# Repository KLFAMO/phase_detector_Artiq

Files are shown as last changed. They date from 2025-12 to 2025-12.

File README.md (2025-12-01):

# Phase Detector for Frequencies from 0 to 200 MHz

## Description

This is a phase detector designed to measure phase differences for input frequencies ranging from 0 to approximately 200 MHz. The device includes configurable frequency dividers for each input channel.

An STM32 microcontroller is used to manage the operational parameters of the detector and its components. These settings can be modified via an Ethernet interface by sending specific commands to the device.

## Features

- **Frequency Range**: 0 - 200 MHz (may change, depending on chips availability)
- **Configurable Frequency Dividers** for each input channel
- **STM32 Microcontroller** to manage operational parameters
- **Ethernet Communication** for real-time configuration and monitoring
- **Outputs**:
  - Fast analog output from the phase detector
  - Slow analog output from the phase detector
  - Analog output after passing through a PI controller
- **Standards**: The device is compliant with **Sinara** and **Artic** standards, ensuring compatibility with other systems that adhere to these protocols.

## Communication

The device allows full configuration and monitoring via Ethernet. Users can send commands to the microcontroller to change parameters such as:
- Frequency divider values
- Phase detector settings
- Calibration and diagnostics

## Applications

The phase detector is suitable for a variety of applications, including:
- Laser to optical frequency comb frequency locking
- Laser to laser frequency locking.

## Documentation

Detailed documentation, including schematics, source code, and configuration instructions, will be provided in future releases of the repository.

## commands

`R 1` - read register from `ADDR`, after reading `R` is set to 0

`W 1` - write to register of address `ADDR`, after writing `W` is set to 0

`RV` - red value

`WV` - value to write 

`ADDR` - register address to be red or written

## License

[MIT](https://opensource.org/licenses/MIT)

## Acknowledgments
This work has received funding from the European Partnership on Metrology, co-financed by the European Union’s Horizon Europe Research and Innovation Programme and by the Participating States, under grant number 22IEM01 TOCK.

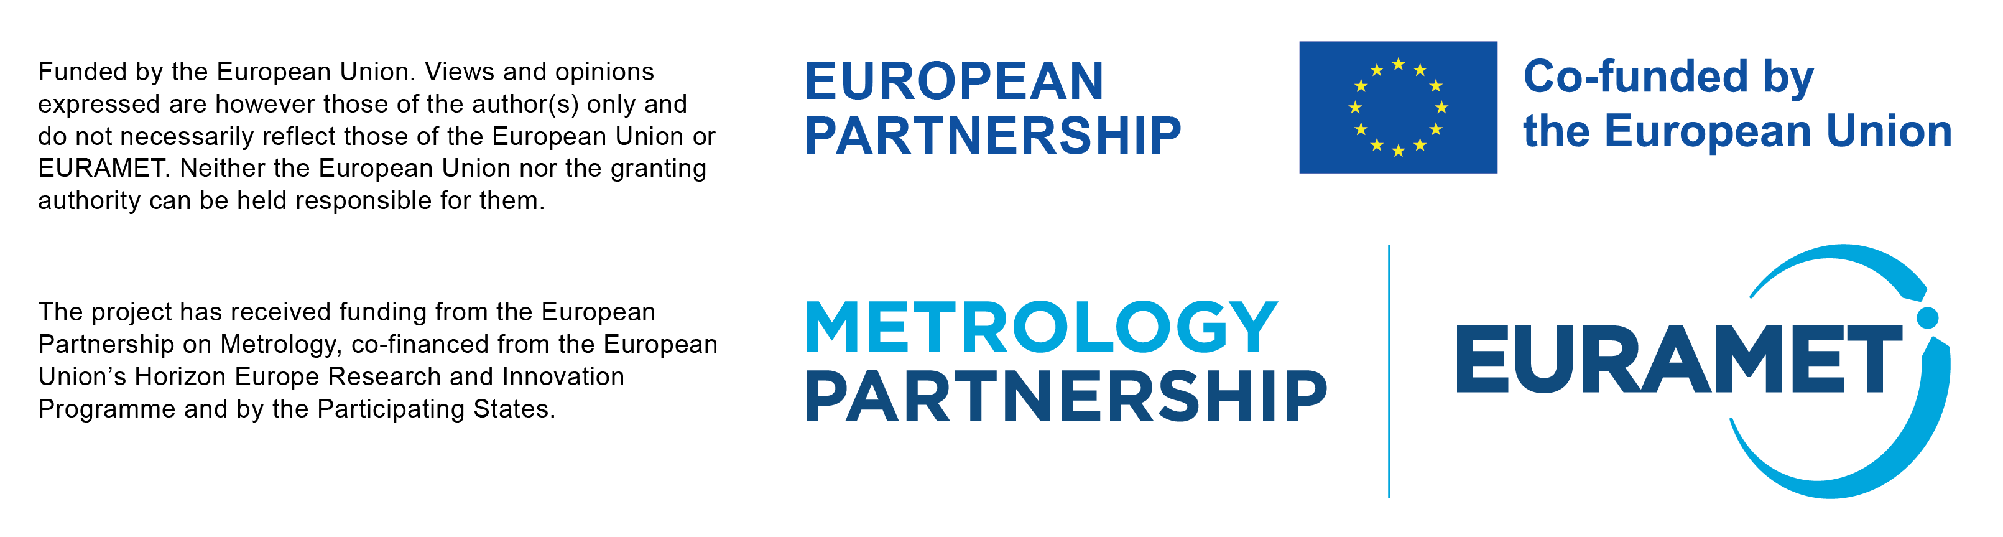
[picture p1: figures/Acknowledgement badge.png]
badge


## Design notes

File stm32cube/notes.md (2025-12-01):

2024-09-02

Checking DAC: bits to voltage

DACIN1 - [SetDAC(0, 65000);]  -> 2.955 V
DACIN1 - [SetDAC(0, 30000);]  -> 1.35 V
DACIN2 - [SetDAC(1, 25000);]  -> 1.125 V
DACIN3 - [SetDAC(2, 20000);]  -> 0.882 V
DACIN4 - [SetDAC(3, 10000);]  -> 0.425 V

Checking time factor
1st test (from Mehrdad program)
10ms in program ->  300ms

Test - transistors
val set in DAC table -> current measured by multimeter  (another board)

L1:
start: -0.1A
0.0V -> 0.1A
0.1V -> -0.11A (-0.42A)
1.0V -> -0.18A (-0.94A)
2.0V -> -0.38A
-1.0V -> 0.2A
-2.0V -> 0.4A (1.89A)

L2:
start: -0.38A
0.0V -> 0.38A
0.1V -> -0.41A (-0.4A)
1.0V -> -0.93A (-0.92A)
2.0V -> -1.85
-1.0V -> 0.93A
-2.0V -> 1.86A (1.85A)

L3:
start: -0.36A
0.0V -> -0.36A
0.1V -> -0.39A (-0.39A)
1.0V -> -0.9A (-0.89A)
2.0V -> -1.8A
-1.0V -> 0.9A 
-2.0V -> 1.8A (1.79A)

2024-09-03
cur1, cur2 and cur3 = 5mV if no current applied (just after starting uC and without load and high power supply)

L1: DAC_set=0V -> DACIN1_mes=0.48V

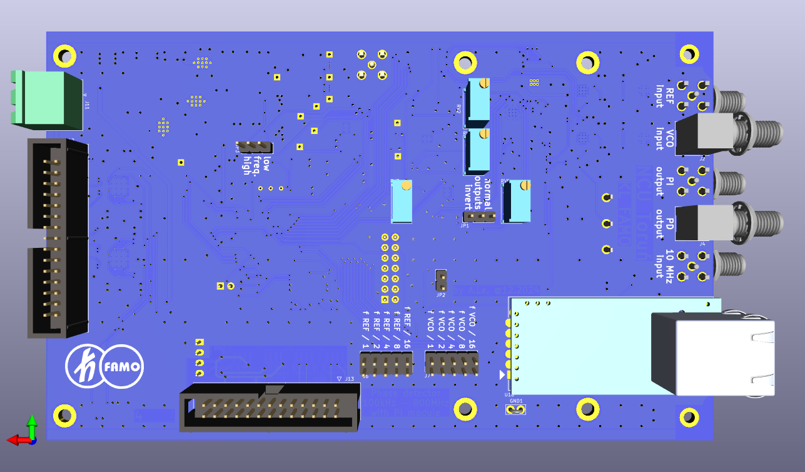
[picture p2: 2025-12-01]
kicad/model/HF_phase_detector_bottom.png

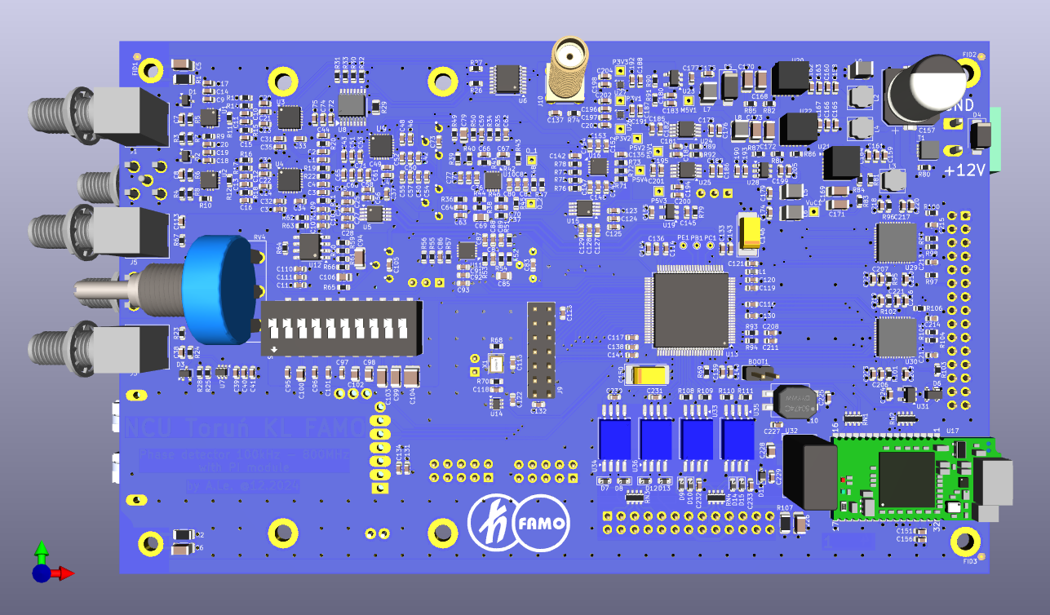
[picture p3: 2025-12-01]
kicad/model/HF_phase_detector_top.png

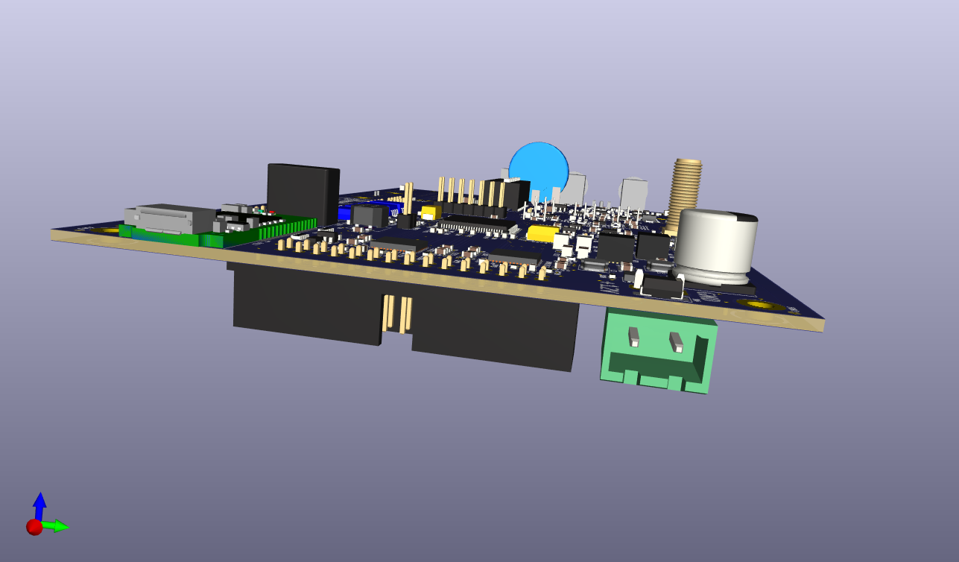
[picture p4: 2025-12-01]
kicad/model/HF_phase_detector_right.png

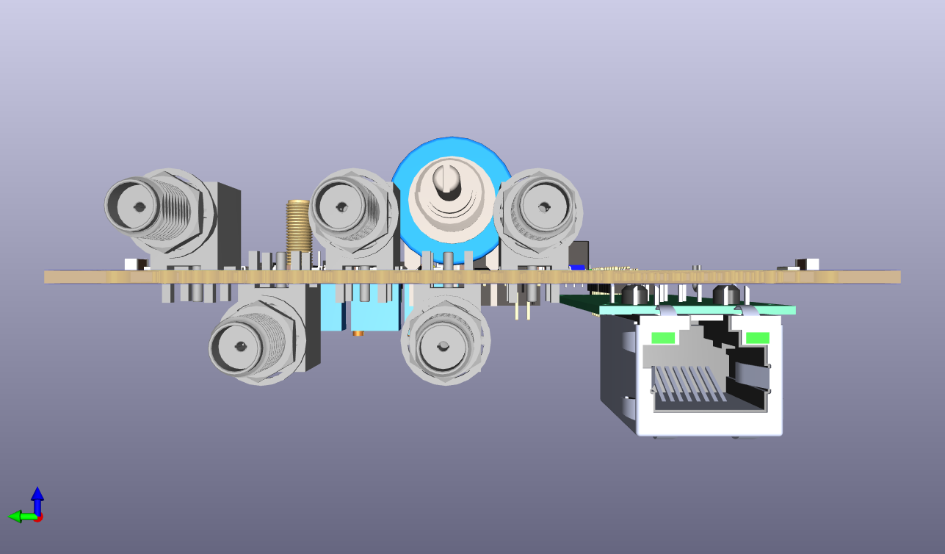
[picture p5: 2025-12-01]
kicad/model/HF_phase_detector_left.png

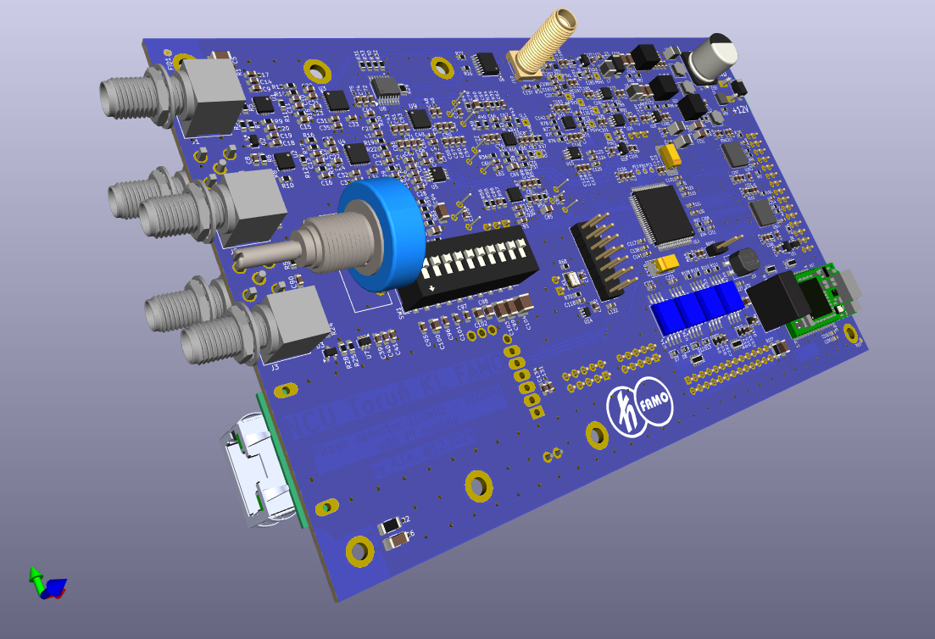
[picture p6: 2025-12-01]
kicad/model/HF_phase_detector.png

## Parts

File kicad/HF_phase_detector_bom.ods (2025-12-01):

Source: | D:\Projekty\FAMO\HF_phase_detector\HF_phase_detector.kicad_sch
Date: | 07.01.2025 11:11:47
Tool: | Eeschema 7.0.11
Generator: | C:\Program Files\KiCad\bin\scripting\plugins/bom_csv_grouped_by_value.py
Component Count: | 429
Item | Qty | Reference(s) | Value | LibPart | Footprint | Datasheet | Comm | Sim.Device | Sim.Enable | Sim.Pins
1 | 0 | BOOT1 | DNP | Connector_Generic:Conn_01x02 | Connector_PinHeader_2.54mm:PinHeader_1x02_P2.54mm_Vertical | ~ | igły 2x1x2,54
2 | 16 | C1, C2, C3, C4, C7, C8, C10, C11, C12, C13, C15, C16, C25, C26, C27, C28 | 15n 25V C0G | Device:C | Capacitor_SMD:C_0603_1608Metric | ~
3 | 3 | C5, C6, C226 | GCJ31BR73A102KXJ1L | Device:C | Capacitor_SMD:C_1206_3216Metric | ~ | 1n 1kV X7R
4 | 14 | C9, C18, C39, C72, C76, C80, C87, C91, C107, C110, C123, C127, C147, C152 | 100p 50V C0G | Device:C | Capacitor_SMD:C_0603_1608Metric | ~
5 | 78 | C14, C19, C21, C22, C23, C24, C31, C32, C33, C34, C37, C40, C46, C47, C50, C51, C57, C58, C64, C68, C74, C77, C81, C88, C92, C108, C111, C115, C116, C119, C122, C124, C128, C130, C133, C134, C136, C138, C139, C148, C151, C153, C155, C163, C164, C167, C177, C178, C180, C181, C182, C189, C191, C192, C193, C194, C195, C196, C197, C198, C199, C206, C207, C209, C210, C212, C213, C214, C215, C216, C217, C218, C219, C224, C230, C231, C232, C233 | 100n 50V X7R | Device:C | Capacitor_SMD:C_0603_1608Metric | ~
6 | 58 | C17, C20, C29, C30, C35, C36, C41, C42, C43, C55, C56, C63, C65, C73, C75, C78, C82, C83, C89, C93, C105, C109, C112, C121, C125, C126, C129, C131, C132, C140, C144, C149, C154, C156, C174, C175, C176, C179, C183, C184, C185, C186, C187, C188, C190, C200, C201, C202, C203, C204, C205, C220, C221, C222, C223, C225, C227, C229 | GRM188R61E106KA73 | Device:C | Capacitor_SMD:C_0603_1608Metric | ~ | 10uF 25V X5R
7 | 10 | C38, C48, C49, C52, C53, C54, C60, C61, C71, C90 | 1n 50V C0G | Device:C | Capacitor_SMD:C_0603_1608Metric | ~
8 | 0 | C44, C45 | DNP | Device:C | Capacitor_SMD:C_0603_1608Metric | ~ | 15n 25V C0G
9 | 4 | C59, C62, C113, C137 | 220p 50V C0G | Device:C | Capacitor_SMD:C_0603_1608Metric | ~
10 | 3 | C66, C67, C70 | ECH-U1C221JX5 | Device:C | Capacitor_SMD:C_0603_1608Metric | ~ | 220p 11V film
11 | 4 | C69, C79, C85, C106 | GRMJN65C1H104... | Device:C | Capacitor_SMD:C_0805_2012Metric | ~ | 100n 50V C0G 0704
12 | 4 | C84, C86, C135, C142 | 22p 50V C0G | Device:C | Capacitor_SMD:C_0603_1608Metric | ~
13 | 2 | C94, C103 | ECH-U1C223JX5 | Device:C | Capacitor_SMD:C_1206_3216Metric | ~ | 22n 16V film
14 | 1 | C95 | ECH-U1C101GX5 | Device:C | Capacitor_SMD:C_0603_1608Metric | ~ | 100p 16V film
15 | 1 | C96 | ECH-U1C471GX5 | Device:C | Capacitor_SMD:C_0603_1608Metric | ~ | 470p 16V film
16 | 1 | C97 | ECH-U1C222GX5 | Device:C | Capacitor_SMD:C_0603_1608Metric | ~ | 2,2n 16V film
17 | 1 | C98 | ECH-U1C103JX5 | Device:C | Capacitor_SMD:C_0805_2012Metric | ~ | 10n 16V film
18 | 1 | C99 | ECH-U1C473GX5 | Device:C | Capacitor_SMD:C_1206_3216Metric | ~ | 47n 16V film
19 | 1 | C100 | ECH-U1H221GX5 | Device:C | Capacitor_SMD:C_0805_2012Metric | ~ | 220p 50V film
20 | 1 | C101 | ECH-U1C102JX5 | Device:C | Capacitor_SMD:C_0603_1608Metric | ~ | 1n 16V film
21 | 1 | C102 | ECH-U1C472GX5 | Device:C | Capacitor_SMD:C_0805_2012Metric | ~ | 4,7n 16V film
22 | 1 | C104 | ECH-U1C104GX5 | Device:C | Capacitor_SMD:C_1210_3225Metric | ~ | 100n 16V film
23 | 2 | C114, C117 | 2u2 10V X7R | Device:C | Capacitor_SMD:C_0603_1608Metric | ~
24 | 2 | C118, C145 | 15p 50V C0G | Device:C | Capacitor_SMD:C_0603_1608Metric | ~
25 | 3 | C120, C141, C143 | GCM188R71E105KA64J | Device:C | Capacitor_SMD:C_0603_1608Metric | ~ | 1uF 25V X7R
26 | 2 | C146, C150 | 293D107X9010C2TE3 | Device:C_Polarized | Capacitor_Tantalum_SMD:CP_EIA-7132-28_AVX-C | ~ | 100u 6,3V tantal case C
27 | 1 | C157 | AEA1010471M025R | Device:C_Polarized | Capacitor_SMD:CP_Elec_10x10 | ~ | ≥ 470u, ≥ 20V, ≥ 5000h
28 | 7 | C158, C159, C160, C161, C162, C165, C166 | GRM188R6YA106MA73 | Device:C | Capacitor_SMD:C_0603_1608Metric | ~ | 10uF 35V X5R
29 | 6 | C168, C169, C170, C171, C172, C173 | GRM31CR61A476KE15L | Device:C | Capacitor_SMD:C_1206_3216Metric | ~ | 47u 10V X5R
30 | 2 | C208, C211 | 82p 50V C0G | Device:C | Capacitor_SMD:C_0603_1608Metric | ~
31 | 1 | C228 | 1n 100V C0G | Device:C | Capacitor_SMD:C_0805_2012Metric | ~
32 | 3 | D1, D2, D3 | BAT54SW... | Diode:BAT54S | Package_TO_SOT_SMD:SOT-323_SC-70 | https://assets.nexperia.com/documents/data-sheet/BAT54SW.pdf
33 | 1 | D4 | SMAJ15AC | Diode:SD12_SOD323 | Diode_SMD:D_SMA | https://www.littelfuse.com/~/media/electronics/datasheets/tvs_diode_arrays/littelfuse_tvs_diode_array_sd_c_datasheet.pdf.pdf
34 | 1 | D5 | STPS2L30A | Device:D_Schottky_Filled | Diode_SMD:D_SMA | ~
35 | 1 | D6 | WE 8240136 | Power_Protection:PRTR5V0U2X | Package_TO_SOT_SMD:SOT-143 | https://assets.nexperia.com/documents/data-sheet/PRTR5V0U2X.pdf | PRTR5V0U2X
36 | 8 | D7, D8, D9, D10, D12, D13, D14, D15 | TS4148C RZG | Device:D_Filled | Diode_SMD:D_0603_1608Metric | ~ |  | D |  | 1=K 2=A
37 | 1 | D11 | SD05.TCT | c3Av2_A-rescue:D_Zener_ALT-Device | Diode_SMD:D_SOD-323
42 | 5 | J1, J2, J3, J4, J5 | RF2-49B-T-00-50-G-HDW | Connector:Conn_Coaxial | Connector_Coaxial:SMA_Amphenol_132203-12_Horizontal | ~ | '132203
43 | 2 | J6, J7 | igły 2x5x2,54mm | Connector_Generic:Conn_02x05_Odd_Even | Connector_PinHeader_2.54mm:PinHeader_2x05_P2.54mm_Vertical | ~
44 | 0 | J9 | DNP | Connector_Generic:Conn_02x07_Odd_Even | Connector_PinHeader_2.54mm:PinHeader_2x07_P2.54mm_Vertical | ~ | igły 2x7x2,54mm
45 | 1 | J10 | SMA6251A1-3GT50G-50 | Connector:Conn_Coaxial | Connector_Coaxial:SMA_Amphenol_132291-12_Vertical | ~
46 | 1 | J11 | MSTBA 2,5/ 2-G-5,08 1757242 | Connector_Generic:Conn_01x02 | Connector_Phoenix_MSTB:PhoenixContact_MSTBA_2,5_2-G-5,08_1x02_P5.08mm_Horizontal | ~
47 | 1 | J12 | N2530-6002-RB | Connector_Generic:Conn_02x15_Odd_Even | Connector_IDC:IDC-Header_2x15_P2.54mm_Vertical | ~
48 | 1 | J13 | N2526-6002RB | Connector:Conn_01x26_Pin | Connector_IDC:IDC-Header_2x13_P2.54mm_Vertical | ~
49 | 2 | JP1, JP3 | igły 1x3x2,54mm | Jumper:Jumper_3_Open | Connector_PinHeader_2.54mm:PinHeader_1x03_P2.54mm_Vertical | ~
50 | 1 | JP2 | igły 1x2x2,54mm | ff:Jumper_2_Open | Connector_PinHeader_2.54mm:PinHeader_1x02_P2.54mm_Vertical | ~
51 | 1 | L1 | LQM18DN330M70L | Device:L | Inductor_SMD:L_0603_1608Metric | ~ | LQM18DZ330M70L
52 | 3 | L2, L3, L4 | LQH44NN101K03L | Device:L_Ferrite | ff_lib_7:L_MURATA_LQH44 | ~ | ≥ 100uH, >200mA
53 | 5 | L5, L6, L7, L8, L9 | LQH32PN100MNCL | Device:L_Ferrite | Inductor_SMD:L_1210_3225Metric | ~ | ≥ 10uH, ≥ 500mA, 1210
54 | 1 | L10 | 50225C Murata | c100AvA-rescue:L_Core_Ferrite_Coupled_1423-Device | ff_lib_7:L_CommonMode_Murata_5000 | https://www.murata-ps.com/pub/data/magnetics/kmp_5000c.pdf | or 50475C
57 | 2 | R1, R2 | CHV1206-FX-1004E | Device:R | Resistor_SMD:R_1206_3216Metric | ~ | HV732BTTD1004F
58 | 6 | R3, R4, R23, R58, R67, R74 | 49,9R 1% | Device:R | Resistor_SMD:R_0603_1608Metric | ~
59 | 6 | R5, R6, R7, R8, R24, R25 | 680R 1% | Device:R | Resistor_SMD:R_0603_1608Metric | ~
60 | 3 | R9, R10, R28 | 150k 1% | Device:R | Resistor_SMD:R_0603_1608Metric | ~
61 | 16 | R11, R12, R70, R79, R95, R96, R97, R98, R99, R100, R101, R102, R103, R104, R105, R106 | 100R 1% | Device:R | Resistor_SMD:R_0603_1608Metric | ~
62 | 2 | R13, R16 | 49,9k 1% | Device:R | Resistor_SMD:R_0603_1608Metric | ~
63 | 9 | R14, R15, R17, R18, R69, R108, R109, R110, R111 | 1k 1% | Device:R | Resistor_SMD:R_0603_1608Metric | ~
64 | 12 | R19, R20, R21, R22, R32, R33, R34, R35, R37, R40, R43, R45 | 200R 1% | Device:R | Resistor_SMD:R_0603_1608Metric | ~
65 | 2 | R26, R27 | 60,4k 1% | Device:R | Resistor_SMD:R_0603_1608Metric | ~
66 | 1 | R29 | 200R 1% | Device:R | Resistor_SMD:R_0805_2012Metric | ~
67 | 2 | R30, R31 | 10R 1% | Device:R | Resistor_SMD:R_0603_1608Metric | ~
68 | 7 | R36, R38, R47, R48, R53, R55, R57 | 3k6 1% | Device:R | Resistor_SMD:R_0603_1608Metric | ~
69 | 5 | R39, R41, R42, R44, R46 | 36k 1% | Device:R | Resistor_SMD:R_0603_1608Metric | ~
70 | 18 | R49, R50, R52, R54, R65, R66, R68, R71, R72, R73, R75, R78, R80, R82, R83, R87, R89, R92 | 10k 1% | Device:R | Resistor_SMD:R_0603_1608Metric | ~
71 | 2 | R51, R56 | 1k2 1% | Device:R | Resistor_SMD:R_0603_1608Metric | ~
72 | 1 | R59 | 475R 1% | Device:R | Resistor_SMD:R_0603_1608Metric | ~
73 | 1 | R60 | 965R 1% | Device:R | Resistor_SMD:R_0603_1608Metric | ~
74 | 1 | R61 | 4,75k 1% | Device:R | Resistor_SMD:R_0603_1608Metric | ~
75 | 5 | R62, R63, R64, R81, R86 | 100k 1% | Device:R | Resistor_SMD:R_0603_1608Metric | ~
76 | 2 | R76, R77 | 30k 1% | Device:R | Resistor_SMD:R_0603_1608Metric | ~
77 | 2 | R84, R85 | 4,32k 1% | Device:R | Resistor_SMD:R_0603_1608Metric | ~
78 | 1 | R88 | 2,26k 1% | Device:R | Resistor_SMD:R_0603_1608Metric | ~
79 | 1 | R90 | 22k 1% | Device:R | Resistor_SMD:R_0603_1608Metric | ~
80 | 1 | R91 | 70,6k 1% | Device:R | Resistor_SMD:R_0603_1608Metric | ~
81 | 2 | R93, R94 | 220R 1% | Device:R | Resistor_SMD:R_0603_1608Metric | ~
82 | 1 | R107 | HV732BTTD1004F | Device:R | Resistor_SMD:R_1206_3216Metric | ~
83 | 2 | RN1, RN2 | CAT16-220J4LF | Device:R_Pack04 | Resistor_SMD:R_Array_Concave_4x0603 | ~
84 | 1 | RN3 | CAT16-102J4LF | Device:R_Pack04 | Resistor_SMD:R_Array_Concave_4x0603 | ~
85 | 1 | RN4 | CAT16-471J4LF | Device:R_Pack04 | Resistor_SMD:R_Array_Concave_4x0603 | ~
86 | 1 | RV1 | 3296Y-1-502LF | Device:R_Potentiometer | Potentiometer_THT:Potentiometer_Bourns_3296Y_Vertical | ~ | T93YB103KT20
87 | 3 | RV2, RV3, RV5 | 3296Y-1-103LF | Device:R_Potentiometer | Potentiometer_THT:Potentiometer_Bourns_3296Y_Vertical | ~ | T93YB103KT20
88 | 1 | RV4 | 3856A-286-103AL | PID_FAMO_v2-rescue:R_POT-Device | ff_lib_7:Potentiometer_Bourns_3856A-286_horizontal | https://www.bourns.com/docs/Product-Datasheets/385126.pdf
89 | 1 | SW1 | A6S-0101-H | Switch:SW_DIP_x10 | Button_Switch_SMD:SW_DIP_SPSTx10_Slide_9.78x27.58mm_W8.61mm_P2.54mm | ~
90 | 1 | T1 | DMP3007SFG-7 | Transistor_FET:DMP3013SFV | ff_lib_7:Diodes_PowerDI3333-8 | https://www.diodes.com/assets/Datasheets/DMP3007SFG.pdf | DMP4013LFG-7
91 | 2 | U1, U2 | TLV3605RVKx | Comparator:LTC6754xUD | Package_DFN_QFN:QFN-12-1EP_3x3mm_P0.5mm_EP1.65x1.65mm_ThermalVias | https://www.ti.com/lit/ds/symlink/tlv3604.pdf
92 | 2 | U3, U4 | CDCM1804RGET | ff:CDCM1804RGET | Package_DFN_QFN:QFN-24-1EP_4x4mm_P0.5mm_EP2.15x2.15mm_ThermalVias | https://www.ti.com/lit/ds/symlink/cdcm1804.pdf
93 | 1 | U5 | LVELT23 | ff:LVELT23 | Package_SO:MSOP-8_3x3mm_P0.65mm | https://www.ti.com/lit/ds/symlink/sn65lvelt23.pdf
94 | 1 | U6 | TBD62003AFNG,EL | Transistor_Array:ULN2003 | Package_SO:SSOP-16_4.4x5.2mm_P0.65mm | https://toshiba.semicon-storage.com/info/TBD62003AFG_datasheet_en_20150724.pdf
95 | 1 | U7 | TLV3603DCKx | Comparator:LTC6752xSC6-1 | Package_TO_SOT_SMD:SOT-363_SC-70-6 | https://www.ti.com/lit/ds/symlink/tlv3601.pdf
96 | 1 | U8 | HMC439QS16GE(TR) | ff:HMC439QS16G | ff_lib_7:QS16GE_ADI | https://www.analog.com/media/en/technical-documentation/data-sheets/hmc439.pdf
97 | 1 | U9 | HMC984LP4E | ff:HMC984LP4E | Package_DFN_QFN:QFN-24-1EP_4x4mm_P0.5mm_EP2.8x2.8mm_ThermalVias | https://www.analog.com/media/en/technical-documentation/data-sheets/hmc984.pdf | https://www.analog.com/media/en/technical-documentation/evaluation-documentation/hmc983lp5e_eval_pcb_schematic.pdf
98 | 3 | U10, U11, U16 | OPA2863AIDSNR | Amplifier_Operational:LTC6269xDD | Package_DFN_QFN:DFN-10-1EP_3x3mm_P0.5mm_EP1.65x2.38mm_ThermalVias | https://www.ti.com/lit/ds/symlink/opa2863a.pdf
99 | 1 | U12 | OPA2206ADR | Amplifier_Operational:OPA2277 | Package_SO:SOIC-8_3.9x4.9mm_P1.27mm | https://www.ti.com/lit/ds/symlink/opa2206.pdf
100 | 1 | U13 | STM32H743VITx | MCU_ST_STM32H7:STM32H743VITx | Package_QFP:LQFP-100_14x14mm_P0.5mm | https://www.st.com/resource/en/datasheet/stm32h743vi.pdf
101 | 1 | U14 | 74AUP1G157GW,125 | ff:1G157 | Package_TO_SOT_SMD:SOT-363_SC-70-6 | https://assets.nexperia.com/documents/data-sheet/74AUP1G157.pdf
102 | 1 | U15 | DAC8550IxDGK | Analog_DAC:DAC8550IxDGK | Package_SO:MSOP-8_3x3mm_P0.65mm | https://www.ti.com/lit/ds/symlink/dac8550.pdf
103 | 1 | U17 | STLINK-V3MODS | ff:STLINK-V3MODS | ff_lib_7:STLINK-V3MODS | https://www.st.com/content/ccc/resource/technical/document/user_manual/group1/00/14/17/68/0f/01/48/01/DM00555046/files/DM00555046.pdf/jcr:content/translations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
104 | 1 | U18 | USR-TCP232-T2 | ff:USR-TCP232-T2 | ff_lib_7:USR-TC232-T2
105 | 2 | U19, U31 | 24AA02E48T-I/OT | Memory_EEPROM:24AA02-OT | Package_TO_SOT_SMD:SOT-23-5 | https://ww1.microchip.com/downloads/en/DeviceDoc/24AA02E48-24AA025E48-24AA02E64-24AA025E64-Data-Sheet-20002124H.pdf
106 | 3 | U20, U21, U22 | TPSM5601R5Hx | ff:TPSM5601R5HRDAR | ff_lib_7:15-B3QFN (5x5,5) | https://www.ti.com/lit/ds/symlink/tpsm5601r5he.pdf
107 | 1 | U23 | TPS72301DBV | ff:TPS72301DBV | Package_TO_SOT_SMD:SOT-23-5 | http://www.ti.com/lit/ds/symlink/tps723.pdf
108 | 2 | U24, U25 | LP2966IMM-5050/NOPB | ff:LP2966IMM-5050_NOPB | Package_SO:VSSOP-8_3.0x3.0mm_P0.65mm | https://www.ti.com/lit/ds/symlink/lp2966.pdf
109 | 2 | U26, U27 | TLV7163030PDPQT | ff:TLV7163030PDPQT | ff_lib_7:DFN-6-1EP_1.2x1.2mm_P0.4mm_EP0.3x0.94mm_ff | https://www.ti.com/lit/ds/symlink/tlv716p.pdf
110 | 1 | U28 | REF3450TIDBVR | ff:REF34xxRDBVR | Package_TO_SOT_SMD:SOT-23-6 | https://www.ti.com/lit/ds/symlink/ref3425.pdf
111 | 2 | U29, U30 | SN65MLVD040RGZT | ff:SN65MLVD040 | ff_lib_7:VQFN-48-1EP_7x7mm_P0.5mm_EP4.1x4.1mm_ThermalVias | https://www.ti.com/lit/ds/symlink/sn65mlvd040.pdf
112 | 1 | U32 | CRE1S1205SC | Regulator_Switching:CRE1S1205SC | Converter_DCDC:Converter_DCDC_Murata_CRE1xxxxxxSC_THT | http://power.murata.com/datasheet?/data/power/ncl/kdc_cre1.pdf | TBA1-1211, IE1205SH
113 | 4 | U33, U34, U35, U36 | TLP2270(TP4,E | Isolator:HCPL-063A | Package_SO:SOIC-8_7.5x5.85mm_P1.27mm | https://toshiba.semicon-storage.com/info/TLP2270_datasheet_en_20191126.pdf
114 | 1 | X1 | ASE-10.000MHZ-L-C-T | Oscillator:ASE-xxxMHz | ff_lib_7:Oscillator_SMD_Abracon_ASE-4Pin_3.2x2.5mm | http://www.abracon.com/Oscillators/ASV.pdf

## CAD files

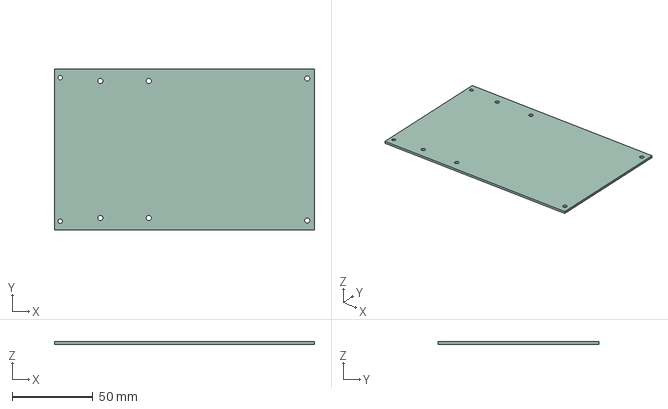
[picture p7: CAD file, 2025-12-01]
kicad/model/artiq_base.step
161.0 x 100.0 x 1.58 mm

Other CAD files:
kicad/model/artiq_base.FCStd

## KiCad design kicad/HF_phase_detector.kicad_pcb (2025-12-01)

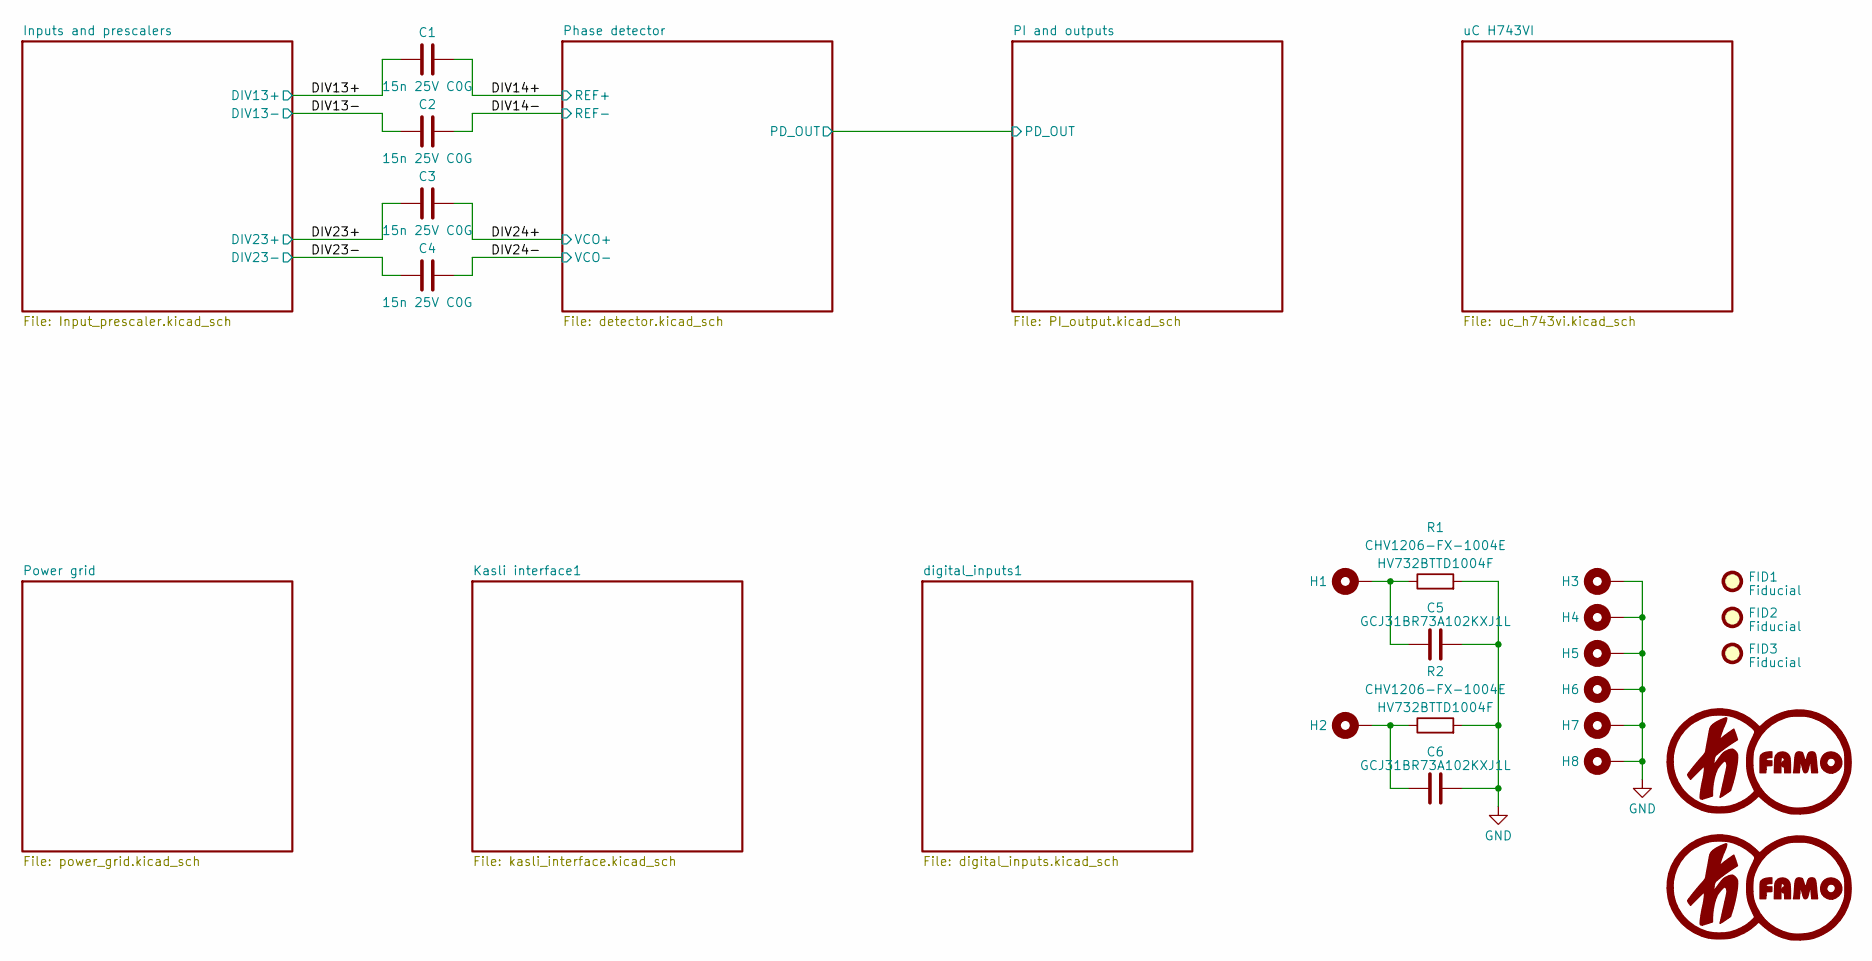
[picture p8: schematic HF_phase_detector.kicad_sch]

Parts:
C1, C2, C3, C4: 15n 25V C0G; C_0603_1608Metric
C5, C6: GCJ31BR73A102KXJ1L; C_1206_3216Metric
FID1, FID2, FID3: Fiducial; Fiducial_0.5mm_Mask1.5mm
G1, G2: LOGO; kl_famo_logo_small
H1, H2: MountingHole_Pad; MountingHole_2.7mm_M2.5_DIN965_Pad
H3, H4, H5, H6, H7, H8: MountingHole_Pad; MountingHole_3.2mm_M3_DIN965_Pad
R1, R2: CHV1206-FX-1004E; R_1206_3216Metric

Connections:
/DIV13-: C2.2; also elsewhere on the board
/DIV14-: C2.1; also elsewhere on the board
/DIV23+: C3.2; also elsewhere on the board
/DIV23-: C4.2; also elsewhere on the board
/DIV24+: C3.1; also elsewhere on the board
/DIV24-: C4.1; also elsewhere on the board
unnamed: C5.1, H1.1, R1.1
unnamed: C6.1, H2.1, R2.1

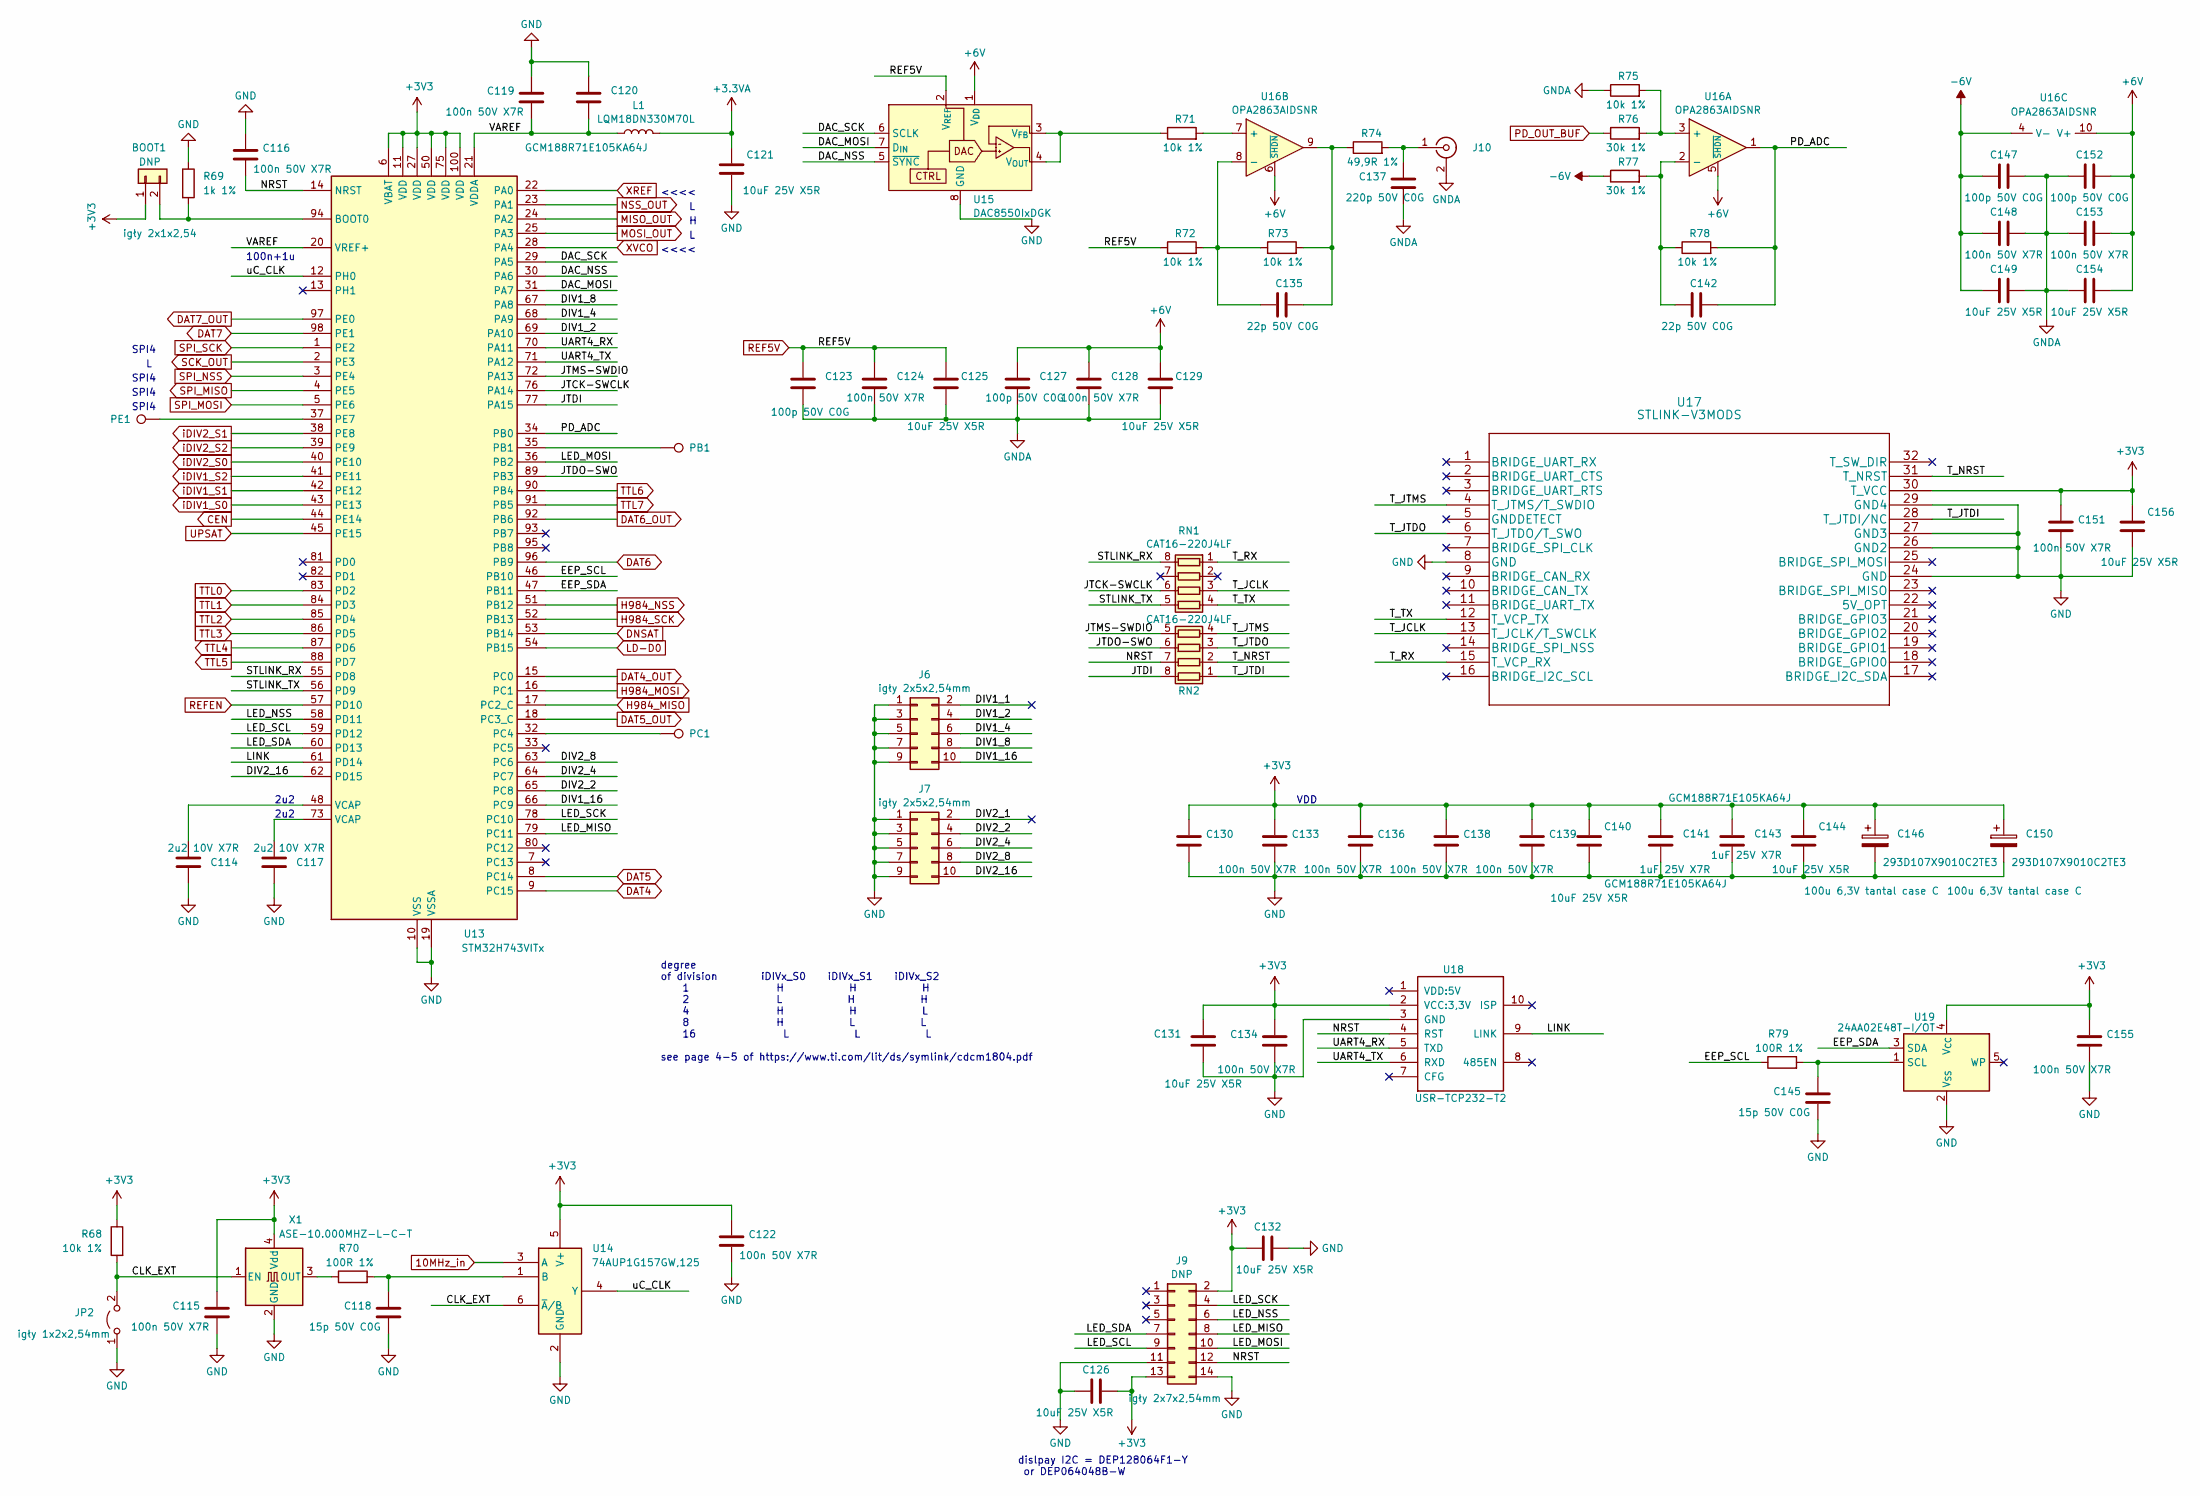
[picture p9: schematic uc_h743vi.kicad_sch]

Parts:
BOOT1: DNP; PinHeader_1x02_P2.54mm_Vertical
C114, C117: 2u2 10V X7R; C_0603_1608Metric
C115, C116, C119, C122, C124, C128, C130, C133, C134, C136, C138, C139, C148, C151, C153, C155: 100n 50V X7R; C_0603_1608Metric
C118, C145: 15p 50V C0G; C_0603_1608Metric
C120, C141, C143: GCM188R71E105KA64J; C_0603_1608Metric
C121, C125, C126, C129, C131, C132, C140, C144, C149, C154, C156: GRM188R61E106KA73; C_0603_1608Metric
C123, C127, C147, C152: 100p 50V C0G; C_0603_1608Metric
C135, C142: 22p 50V C0G; C_0603_1608Metric
C137: 220p 50V C0G; C_0603_1608Metric
C146, C150: 293D107X9010C2TE3; CP_EIA-7132-28_AVX-C
J6, J7: igły 2x5x2,54mm; PinHeader_2x05_P2.54mm_Vertical
J9: DNP; PinHeader_2x07_P2.54mm_Vertical
J10: SMA6251A1-3GT50G-50; SMA_Amphenol_132291-12_Vertical
JP2: igły 1x2x2,54mm; PinHeader_1x02_P2.54mm_Vertical
L1: LQM18DN330M70L; L_0603_1608Metric
PB1: TestPoint; TestPoint_THTPad_D1.0mm_Drill0.5mm
PC1: TestPoint; TestPoint_THTPad_D1.0mm_Drill0.5mm
PE1: TestPoint; TestPoint_THTPad_D1.0mm_Drill0.5mm
R68, R71, R72, R73, R75, R78: 10k 1%; R_0603_1608Metric
R69: 1k 1%; R_0603_1608Metric
R70, R79: 100R 1%; R_0603_1608Metric
R74: 49,9R 1%; R_0603_1608Metric
R76, R77: 30k 1%; R_0603_1608Metric
RN1, RN2: CAT16-220J4LF; R_Array_Concave_4x0603
U13: STM32H743VITx; LQFP-100_14x14mm_P0.5mm
U14: 74AUP1G157GW,125; SOT-363_SC-70-6
U15: DAC8550IxDGK; MSOP-8_3x3mm_P0.65mm
U16: OPA2863AIDSNR; DFN-10-1EP_3x3mm_P0.5mm_EP1.65x2.38mm_ThermalVias
U17: STLINK-V3MODS
U18: USR-TCP232-T2; USR-TC232-T2
U19: 24AA02E48T-I/OT; SOT-23-5
X1: ASE-10.000MHZ-L-C-T; Oscillator_SMD_Abracon_ASE-4Pin_3.2x2.5mm

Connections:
10MHz_in: U14.3 (A); also elsewhere on the board
/uC H743VI/CLK_EXT: JP2.2 (B), R68.2, U14.6 (~A/B), X1.1 (EN)
/uC H743VI/DAC_MOSI: U13.31 (PA7), U15.7 (D_{IN})
/uC H743VI/DAC_NSS: U13.30 (PA6), U15.5 (~SYNC)
/uC H743VI/DAC_SCK: U13.29 (PA5), U15.6 (SCLK)
/uC H743VI/DIV1_1: J6.2
/uC H743VI/DIV1_2: J6.4, U13.69 (PA10)
/uC H743VI/DIV1_4: J6.6, U13.68 (PA9)
/uC H743VI/DIV1_8: J6.8, U13.67 (PA8)
/uC H743VI/DIV1_16: J6.10, U13.66 (PC9)
/uC H743VI/DIV2_1: J7.2
/uC H743VI/DIV2_2: J7.4, U13.65 (PC8)
/uC H743VI/DIV2_4: J7.6, U13.64 (PC7)
/uC H743VI/DIV2_8: J7.8, U13.63 (PC6)
/uC H743VI/DIV2_16: J7.10, U13.62 (PD15)
/uC H743VI/EEP_SCL: R79.1, U13.46 (PB10)
/uC H743VI/EEP_SDA: U13.47 (PB11), U19.3 (SDA)
/uC H743VI/JTCK-SWCLK: RN1.6 (R3.2), U13.76 (PA14)
/uC H743VI/JTDI: RN2.8 (R1.2), U13.77 (PA15)
/uC H743VI/JTDO-SWO: RN2.6 (R3.2), U13.89 (PB3)
/uC H743VI/JTMS-SWDIO: RN2.5 (R4.2), U13.72 (PA13)
/uC H743VI/LED_MISO: J9.8, U13.79 (PC11)
/uC H743VI/LED_MOSI: J9.10, U13.36 (PB2)
/uC H743VI/LED_NSS: J9.6, U13.58 (PD11)
/uC H743VI/LED_SCK: J9.4, U13.78 (PC10)
/uC H743VI/LED_SCL: J9.9, U13.59 (PD12)
/uC H743VI/LED_SDA: J9.7, U13.60 (PD13)
/uC H743VI/LINK: U13.61 (PD14), U18.9 (LINK)
/uC H743VI/NRST: C116.2, J9.12, RN2.7 (R2.2), U13.14 (NRST), U18.4 (RST)
/uC H743VI/STLINK_RX: RN1.8 (R1.2), U13.55 (PD8)
/uC H743VI/STLINK_TX: RN1.5 (R4.2), U13.56 (PD9)
/uC H743VI/T_JCLK: RN1.3 (R3.1), U17.13 (T_JCLK/T_SWCLK)
/uC H743VI/T_JTDI: RN2.1 (R1.1), U17.28 (T_JTDI/NC)
/uC H743VI/T_JTDO: RN2.3 (R3.1), U17.6 (T_JTDO/T_SWO)
/uC H743VI/T_JTMS: RN2.4 (R4.1), U17.4 (T_JTMS/T_SWDIO)
/uC H743VI/T_NRST: RN2.2 (R2.1), U17.31 (T_NRST)
/uC H743VI/T_RX: RN1.1 (R1.1), U17.15 (T_VCP_RX)
/uC H743VI/T_TX: RN1.4 (R4.1), U17.12 (T_VCP_TX)
/uC H743VI/UART4_RX: U13.70 (PA11), U18.5 (TXD)
/uC H743VI/UART4_TX: U13.71 (PA12), U18.6 (RXD)
/uC H743VI/uC_CLK: U13.12 (PH0), U14.4 (Y)
CEN: U13.44 (PE14); also elsewhere on the board
DAT4: U13.9 (PC15); also elsewhere on the board
DAT4_OUT: U13.15 (PC0); also elsewhere on the board
DAT5: U13.8 (PC14); also elsewhere on the board
DAT5_OUT: U13.18 (PC3_C); also elsewhere on the board
DAT6: U13.96 (PB9); also elsewhere on the board
DAT6_OUT: U13.92 (PB6); also elsewhere on the board
DAT7: U13.98 (PE1); also elsewhere on the board
DAT7_OUT: U13.97 (PE0); also elsewhere on the board
DNSAT: U13.53 (PB14); also elsewhere on the board
H984_MISO: U13.17 (PC2_C); also elsewhere on the board
H984_MOSI: U13.16 (PC1); also elsewhere on the board
H984_NSS: U13.51 (PB12); also elsewhere on the board
H984_SCK: U13.52 (PB13); also elsewhere on the board
LD-D0: U13.54 (PB15); also elsewhere on the board
MISO_OUT: U13.24 (PA2); also elsewhere on the board
MOSI_OUT: U13.25 (PA3); also elsewhere on the board
NSS_OUT: U13.23 (PA1); also elsewhere on the board
unnamed: BOOT1.2, R69.2, U13.94 (BOOT0)
unnamed: C114.2, U13.48 (VCAP)
unnamed: C117.2, U13.73 (VCAP)
unnamed: C135.2, R73.2, R74.1, U16.9
unnamed: C137.2, J10.1 (In), R74.2
unnamed: PB1.1, U13.35 (PB1)
unnamed: PC1.1, U13.32 (PC4)
unnamed: PE1.1, U13.37 (PE7)
unnamed: C118.1, R70.2, U14.1 (B)
unnamed: R71.1, U15.3 (V_{FB}), U15.4 (V_{OUT})
unnamed: R75.2, R76.2, U16.3 (+)
unnamed: R71.2, U16.7 (+)
unnamed: C135.1, R72.2, R73.1, U16.8 (-)
unnamed: C145.1, R79.2, U19.1 (SCL)
unnamed: R70.1, X1.3 (OUT)
PD_OUT_BUF: R76.1; also elsewhere on the board
REF5V: C123.2, C124.2, C125.2, R72.1, U15.2 (V_{REF}); also elsewhere on the board
REFEN: U13.57 (PD10); also elsewhere on the board
SCK_OUT: U13.2 (PE3); also elsewhere on the board
SPI_MISO: U13.4 (PE5); also elsewhere on the board
SPI_MOSI: U13.5 (PE6); also elsewhere on the board
SPI_NSS: U13.3 (PE4); also elsewhere on the board
SPI_SCK: U13.1 (PE2); also elsewhere on the board
TTL0: U13.83 (PD2); also elsewhere on the board
TTL1: U13.84 (PD3); also elsewhere on the board
TTL2: U13.85 (PD4); also elsewhere on the board
TTL3: U13.86 (PD5); also elsewhere on the board
TTL4: U13.87 (PD6); also elsewhere on the board
TTL5: U13.88 (PD7); also elsewhere on the board
TTL6: U13.90 (PB4); also elsewhere on the board
TTL7: U13.91 (PB5); also elsewhere on the board
UPSAT: U13.45 (PE15); also elsewhere on the board
XREF: U13.22 (PA0); also elsewhere on the board
XVCO: U13.28 (PA4); also elsewhere on the board
iDIV1_S0: U13.43 (PE13); also elsewhere on the board
iDIV1_S1: U13.42 (PE12); also elsewhere on the board
iDIV1_S2: U13.41 (PE11); also elsewhere on the board
iDIV2_S0: U13.40 (PE10); also elsewhere on the board
iDIV2_S1: U13.38 (PE8); also elsewhere on the board
iDIV2_S2: U13.39 (PE9); also elsewhere on the board

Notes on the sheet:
VDD
2u2
<<<<
dislpay I2C = DEP128064F1-Y or DEP064048B-W
SPI4
100n+1u
degree of division iDIVx_S0 iDIVx_S1 iDIVx_S2 1 H H H 2 L H H 4 H H L 8 H L L 16 L L L see page 4-5 of https://www.ti.com/lit/ds/symlink/cdcm1804.pdf

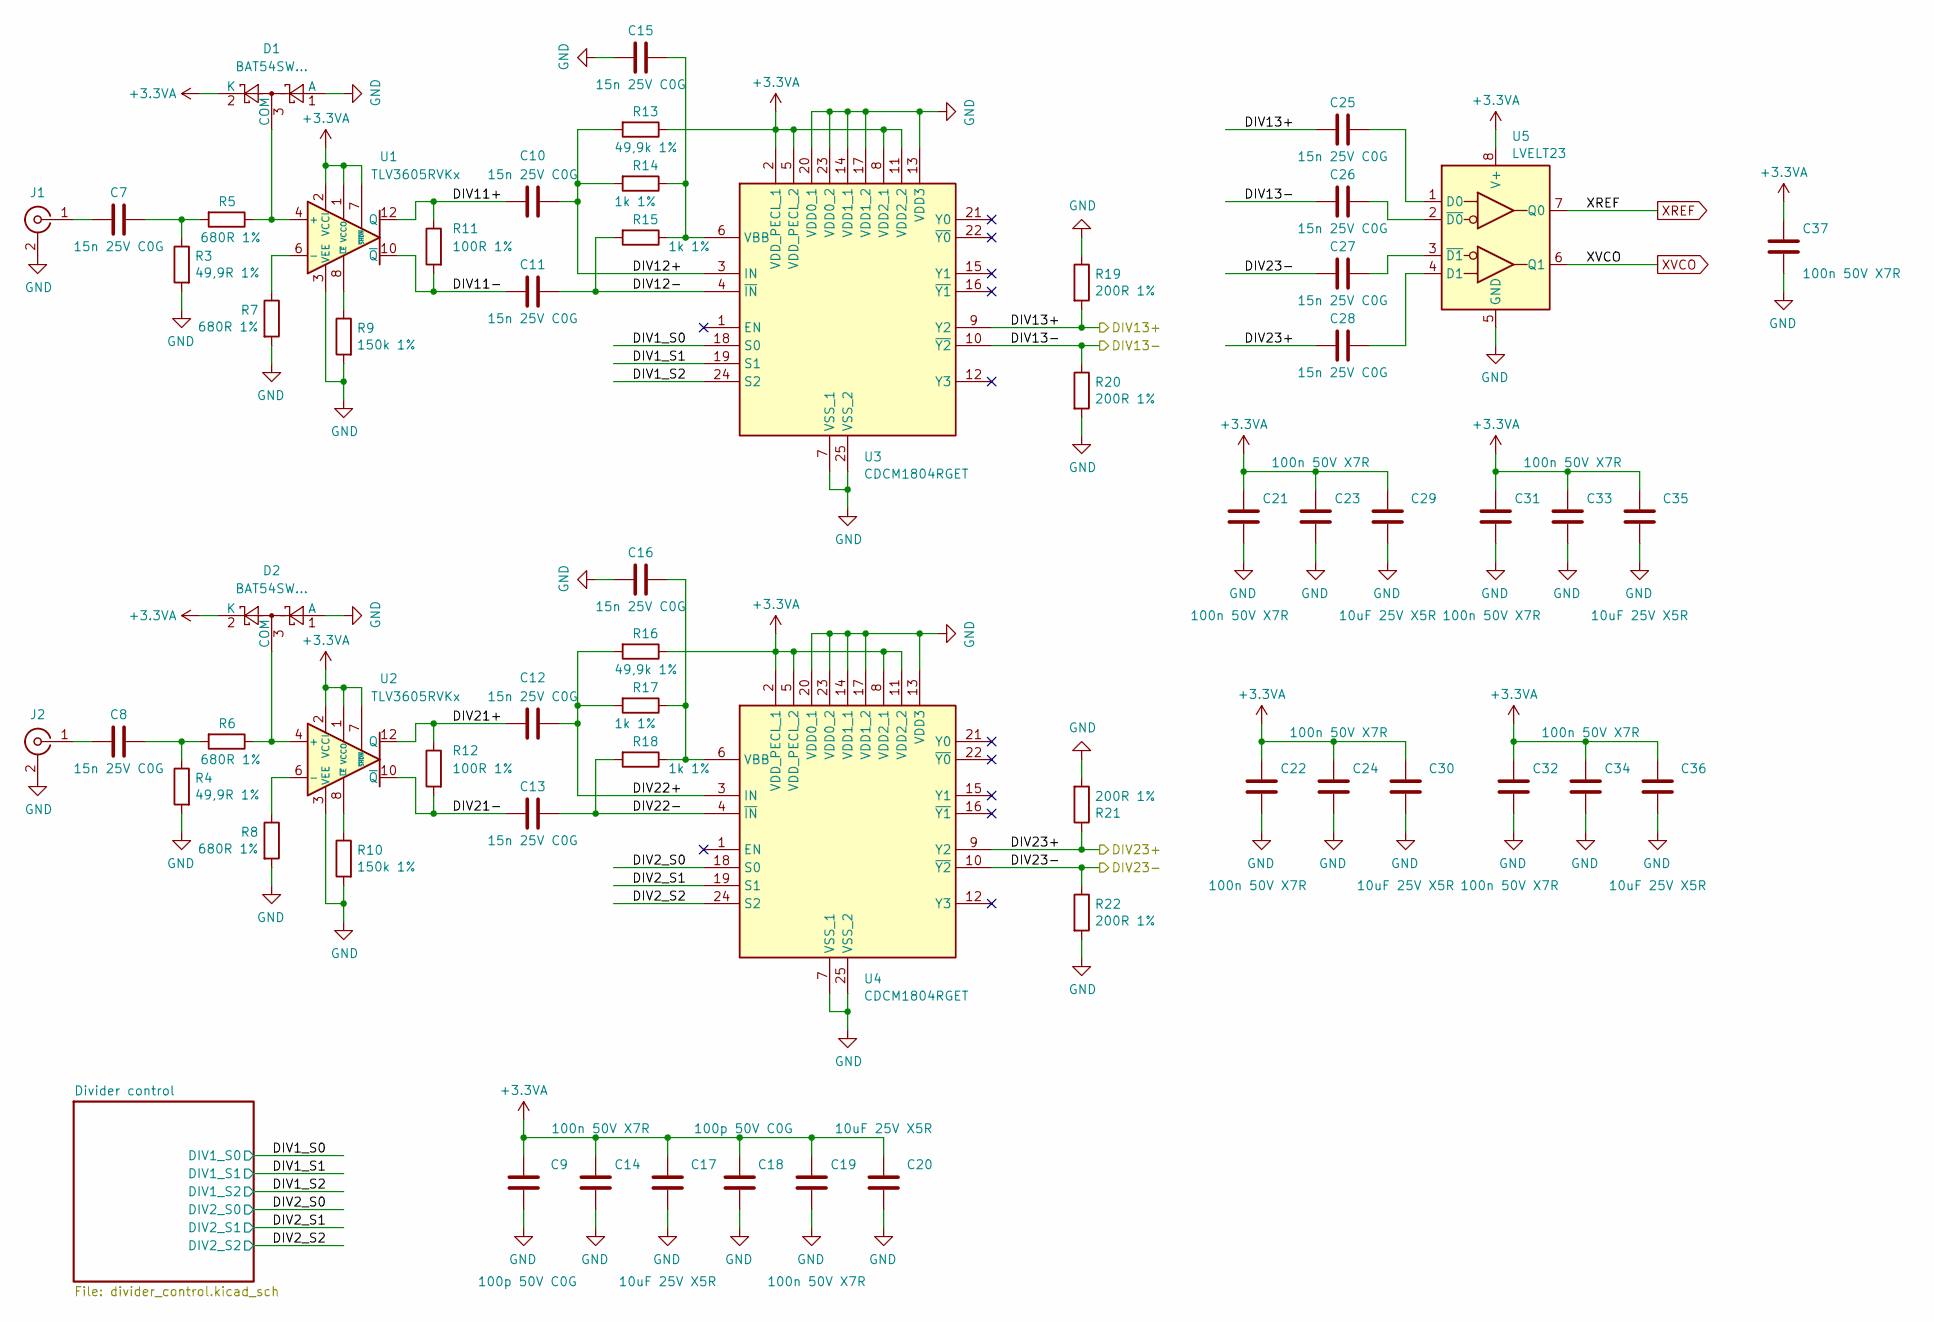
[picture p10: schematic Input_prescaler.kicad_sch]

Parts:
C7, C8, C10, C11, C12, C13, C15, C16, C25, C26, C27, C28: 15n 25V C0G; C_0603_1608Metric
C9, C18: 100p 50V C0G; C_0603_1608Metric
C14, C19, C21, C22, C23, C24, C31, C32, C33, C34, C37: 100n 50V X7R; C_0603_1608Metric
C17, C20, C29, C30, C35, C36: GRM188R61E106KA73; C_0603_1608Metric
D1, D2: BAT54SW...; SOT-323_SC-70
J1, J2: RF2-49B-T-00-50-G-HDW; SMA_Amphenol_132203-12_Horizontal
R3, R4: 49,9R 1%; R_0603_1608Metric
R5, R6, R7, R8: 680R 1%; R_0603_1608Metric
R9, R10: 150k 1%; R_0603_1608Metric
R11, R12: 100R 1%; R_0603_1608Metric
R13, R16: 49,9k 1%; R_0603_1608Metric
R14, R15, R17, R18: 1k 1%; R_0603_1608Metric
R19, R20, R21, R22: 200R 1%; R_0603_1608Metric
U1, U2: TLV3605RVKx; QFN-12-1EP_3x3mm_P0.5mm_EP1.65x1.65mm_ThermalVias
U3, U4: CDCM1804RGET; QFN-24-1EP_4x4mm_P0.5mm_EP2.15x2.15mm_ThermalVias
U5: LVELT23; MSOP-8_3x3mm_P0.65mm

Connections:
/DIV13-: C26.2, R20.1, U3.10 (~Y2); also elsewhere on the board
/DIV23+: C28.2, R21.1, U4.9 (Y2); also elsewhere on the board
/DIV23-: C27.2, R22.1, U4.10 (~Y2); also elsewhere on the board
/Inputs and prescalers/DIV1_S0: U3.18 (S0); also elsewhere on the board
/Inputs and prescalers/DIV1_S1: U3.19 (S1); also elsewhere on the board
/Inputs and prescalers/DIV1_S2: U3.24 (S2); also elsewhere on the board
/Inputs and prescalers/DIV2_S0: U4.18 (S0); also elsewhere on the board
/Inputs and prescalers/DIV2_S1: U4.19 (S1); also elsewhere on the board
/Inputs and prescalers/DIV2_S2: U4.24 (S2); also elsewhere on the board
/Inputs and prescalers/DIV11+: C10.2, R11.1, U1.12 (Q)
/Inputs and prescalers/DIV11-: C11.2, R11.2, U1.10 (~Q)
/Inputs and prescalers/DIV12+: C10.1, R13.2, R14.2, U3.3 (IN)
/Inputs and prescalers/DIV12-: C11.1, R15.2, U3.4 (~IN)
/Inputs and prescalers/DIV21+: C12.2, R12.1, U2.12 (Q)
/Inputs and prescalers/DIV21-: C13.2, R12.2, U2.10 (~Q)
/Inputs and prescalers/DIV22+: C12.1, R16.2, R17.2, U4.3 (IN)
/Inputs and prescalers/DIV22-: C13.1, R18.2, U4.4 (~IN)
unnamed: C7.1, R3.1, R5.2
unnamed: C8.1, R4.1, R6.2
unnamed: D1.3 (COM), R5.1, U1.4 (+)
unnamed: D2.3 (COM), R6.1, U2.4 (+)
unnamed: C8.2, J2.1 (In)
unnamed: R7.1, U1.6 (-)
unnamed: R9.1, U1.8 (~LE)
unnamed: R8.1, U2.6 (-)
unnamed: R10.1, U2.8 (~LE)
unnamed: C15.1, R14.1, R15.1, U3.6 (VBB)
unnamed: C16.1, R17.1, R18.1, U4.6 (VBB)
unnamed: C25.1, U5.1 (D0)
unnamed: C28.1, U5.4 (D1)
unnamed: C26.1, U5.2 (~D0)
unnamed: C27.1, U5.3 (~D1)
XREF: U5.7 (Q0); also elsewhere on the board
XVCO: U5.6 (Q1); also elsewhere on the board

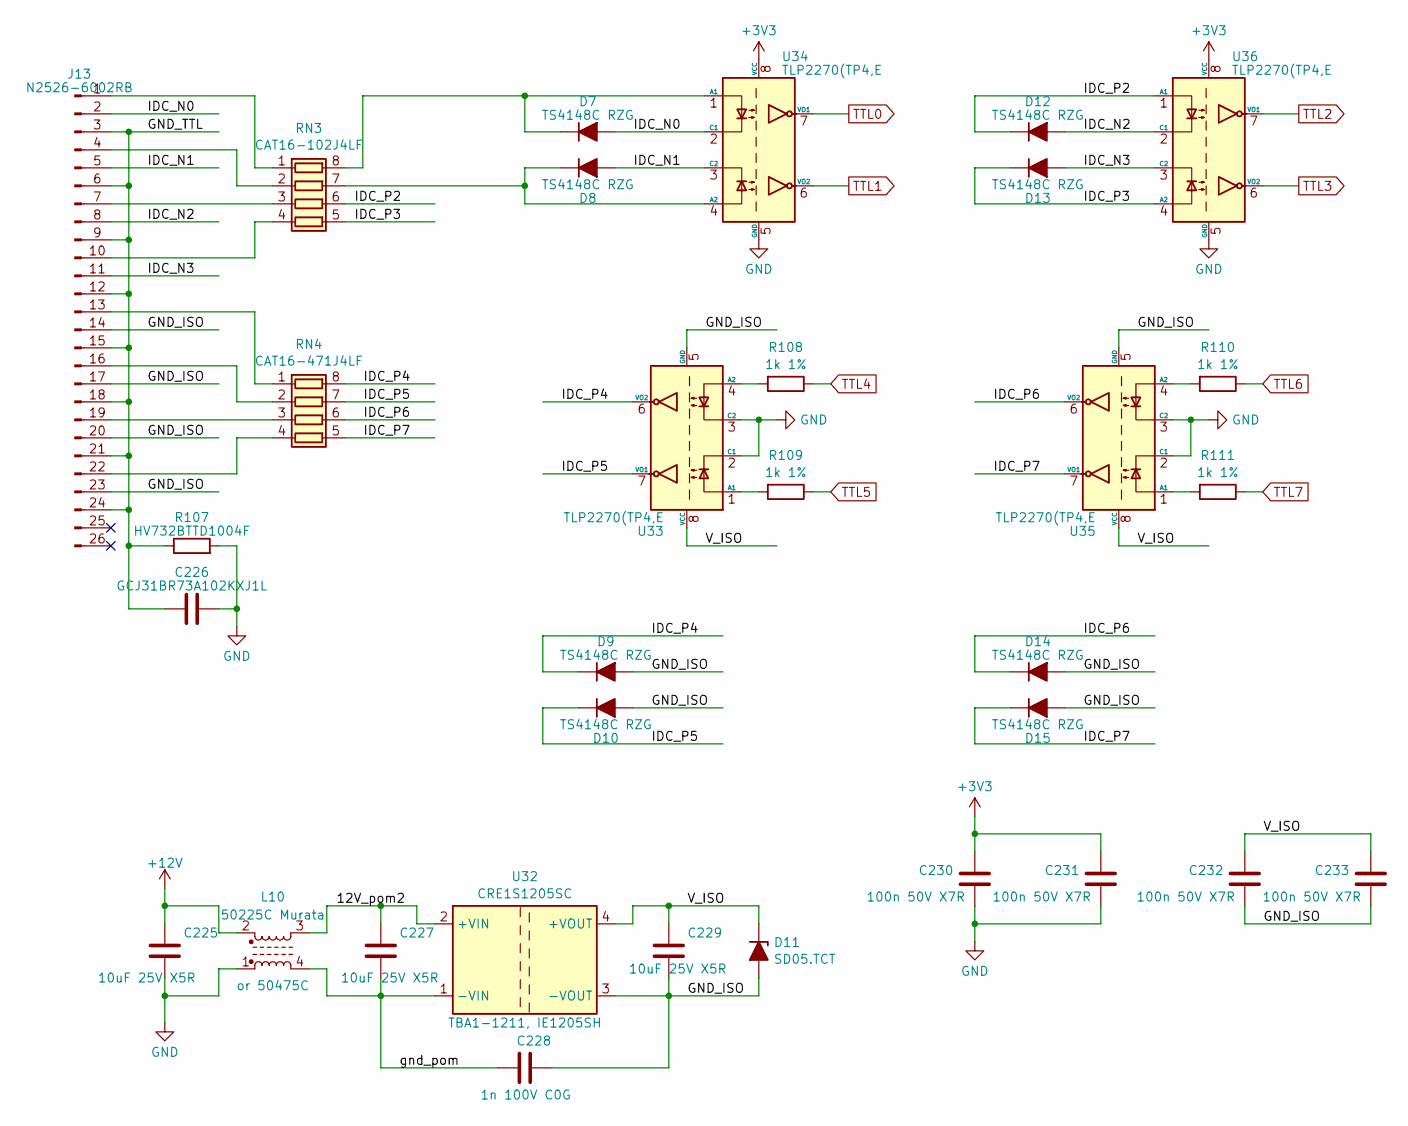
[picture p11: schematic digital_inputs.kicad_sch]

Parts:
C225, C227, C229: GRM188R61E106KA73; C_0603_1608Metric
C226: GCJ31BR73A102KXJ1L; C_1206_3216Metric
C228: 1n 100V C0G; C_0805_2012Metric
C230, C231, C232, C233: 100n 50V X7R; C_0603_1608Metric
D7, D8, D9, D10, D12, D13, D14, D15: TS4148C RZG; D_0603_1608Metric
D11: SD05.TCT; D_SOD-323
J13: N2526-6002RB; IDC-Header_2x13_P2.54mm_Vertical
L10: 50225C Murata; L_CommonMode_Murata_5000
R107: HV732BTTD1004F; R_1206_3216Metric
R108, R109, R110, R111: 1k 1%; R_0603_1608Metric
RN3: CAT16-102J4LF; R_Array_Concave_4x0603
RN4: CAT16-471J4LF; R_Array_Concave_4x0603
U32: CRE1S1205SC; Converter_DCDC_Murata_CRE1xxxxxxSC_THT
U33, U34, U35, U36: TLP2270(TP4,E; SOIC-8_7.5x5.85mm_P1.27mm

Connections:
/digital_inputs1/12V_pom2: C227.2, L10.3, U32.2 (+VIN)
/digital_inputs1/GND_ISO: C228.1, C229.1, C232.2, C233.2, D9.2 (A), D10.2 (A), D11.2 (A), D14.2 (A), D15.2 (A), J13.14, J13.17, J13.20, J13.23, U32.3 (-VOUT), U33.5 (GND), U35.5 (GND)
/digital_inputs1/GND_TTL: C226.1, J13.3, J13.6, J13.9, J13.12, J13.15, J13.18, J13.21, J13.24, R107.1
/digital_inputs1/IDC_N0: D7.2 (A), J13.2, U34.2 (C1)
/digital_inputs1/IDC_N1: D8.2 (A), J13.5, U34.3 (C2)
/digital_inputs1/IDC_N2: D12.2 (A), J13.8, U36.2 (C1)
/digital_inputs1/IDC_N3: D13.2 (A), J13.11, U36.3 (C2)
/digital_inputs1/IDC_P2: D12.1 (K), RN3.6 (R3.2), U36.1 (A1)
/digital_inputs1/IDC_P3: D13.1 (K), RN3.5 (R4.2), U36.4 (A2)
/digital_inputs1/IDC_P4: D9.1 (K), RN4.8 (R1.2), U33.6 (VO2)
/digital_inputs1/IDC_P5: D10.1 (K), RN4.7 (R2.2), U33.7 (VO1)
/digital_inputs1/IDC_P6: D14.1 (K), RN4.6 (R3.2), U35.6 (VO2)
/digital_inputs1/IDC_P7: D15.1 (K), RN4.5 (R4.2), U35.7 (VO1)
/digital_inputs1/V_ISO: C229.2, C232.1, C233.1, D11.1 (K), U32.4 (+VOUT), U33.8 (VCC), U35.8 (VCC)
/digital_inputs1/gnd_pom: C227.1, C228.2, L10.4, U32.1 (-VIN)
unnamed: D7.1 (K), RN3.8 (R1.2), U34.1 (A1)
unnamed: D8.1 (K), RN3.7 (R2.2), U34.4 (A2)
unnamed: J13.1, RN3.1 (R1.1)
unnamed: J13.4, RN3.2 (R2.1)
unnamed: J13.7, RN3.3 (R3.1)
unnamed: J13.10, RN3.4 (R4.1)
unnamed: J13.13, RN4.1 (R1.1)
unnamed: J13.16, RN4.2 (R2.1)
unnamed: J13.19, RN4.3 (R3.1)
unnamed: J13.22, RN4.4 (R4.1)
unnamed: R109.2, U33.1 (A1)
unnamed: R108.2, U33.4 (A2)
unnamed: R111.2, U35.1 (A1)
unnamed: R110.2, U35.4 (A2)
TTL0: U34.7 (VO1); also elsewhere on the board
TTL1: U34.6 (VO2); also elsewhere on the board
TTL2: U36.7 (VO1); also elsewhere on the board
TTL3: U36.6 (VO2); also elsewhere on the board
TTL4: R108.1; also elsewhere on the board
TTL5: R109.1; also elsewhere on the board
TTL6: R110.1; also elsewhere on the board
TTL7: R111.1; also elsewhere on the board

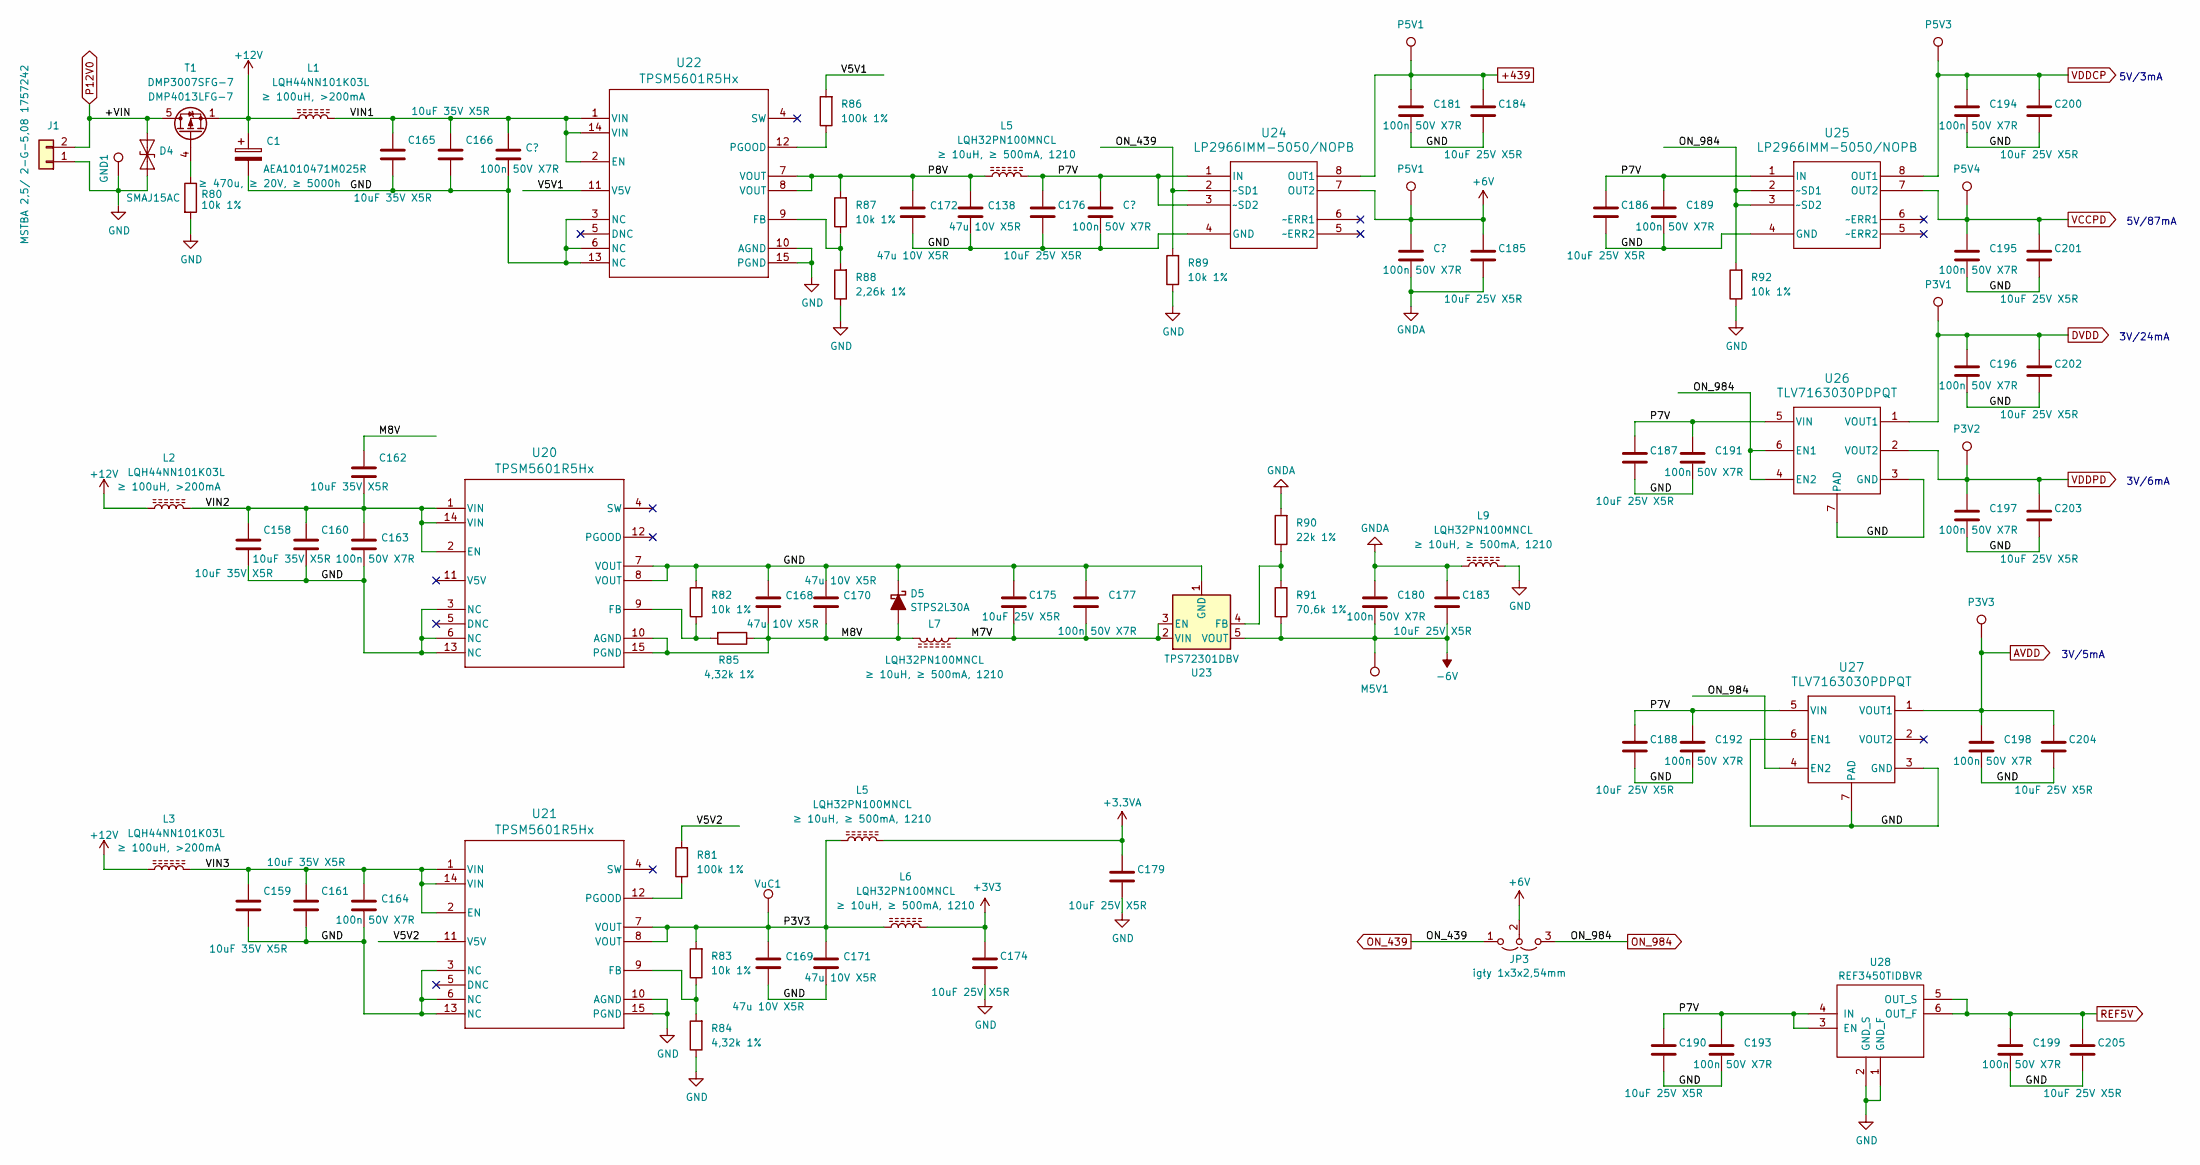
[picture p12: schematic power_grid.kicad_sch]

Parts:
C1: AEA1010471M025R; CP_Elec_10x10
C134, C142, C147, C163, C164, C177, C180, C181, C189, C191, C192, C193, C194, C195, C196, C197, C198, C199: 100n 50V X7R; C_0603_1608Metric
C138, C168, C169, C170, C171, C172: GRM31CR61A476KE15L; C_1206_3216Metric
C158, C159, C160, C161, C162, C165, C166: GRM188R6YA106MA73; C_0603_1608Metric
C174, C175, C176, C179, C183, C184, C185, C186, C187, C188, C190, C200, C201, C202, C203, C204, C205: GRM188R61E106KA73; C_0603_1608Metric
D4: SMAJ15AC; D_SMA
D5: STPS2L30A; D_SMA
GND1: TestPoint; TestPoint_Bridge_Pitch2.54mm_Drill1.0mm
J1: MSTBA 2,5/ 2-G-5,08 1757242; PhoenixContact_MSTBA_2,5_2-G-5,08_1x02_P5.08mm_Horizontal
JP3: igły 1x3x2,54mm; PinHeader_1x03_P2.54mm_Vertical
L1, L2, L3: LQH44NN101K03L; L_MURATA_LQH44
L5, L6, L7, L9: LQH32PN100MNCL; L_1210_3225Metric
M5V1: TestPoint; TestPoint_THTPad_1.5x1.5mm_Drill0.7mm
P3V1, P3V2, P3V3, P5V1, P5V3, P5V4: TestPoint; TestPoint_THTPad_1.5x1.5mm_Drill0.7mm
R80, R82, R83, R87, R89, R92: 10k 1%; R_0603_1608Metric
R81, R86: 100k 1%; R_0603_1608Metric
R84, R85: 4,32k 1%; R_0603_1608Metric
R88: 2,26k 1%; R_0603_1608Metric
R90: 22k 1%; R_0603_1608Metric
R91: 70,6k 1%; R_0603_1608Metric
T1: DMP3007SFG-7; Diodes_PowerDI3333-8
U20, U21, U22: TPSM5601R5Hx; 15-B3QFN (5x5,5)
U23: TPS72301DBV; SOT-23-5
U24, U25: LP2966IMM-5050/NOPB; VSSOP-8_3.0x3.0mm_P0.65mm
U26, U27: TLV7163030PDPQT; DFN-6-1EP_1.2x1.2mm_P0.4mm_EP0.3x0.94mm_ff
U28: REF3450TIDBVR; SOT-23-6
VuC1: TestPoint; TestPoint_THTPad_1.5x1.5mm_Drill0.7mm

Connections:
/Power grid/M7V: C175.1, C177.1, L7.2, U23.2 (VIN), U23.3 (EN)
/Power grid/M8V: C162.2, C168.2, C170.2, D5.2 (A), L7.1, R85.1, U20.10 (AGND), U20.15 (PGND)
/Power grid/V5V1: R86.2, U22.11 (V5V)
/Power grid/V5V2: R81.2, U21.11 (V5V)
/Power grid/VIN2: C158.2, C160.2, C162.1, C163.2, L2.2, U20.1 (VIN), U20.2 (EN), U20.14 (VIN)
/Power grid/VIN3: C159.2, C161.2, C164.2, L3.2, U21.1 (VIN), U21.2 (EN), U21.14 (VIN)
AVDD: C198.2, C204.2, P3V3.1, U27.1 (VOUT1); also elsewhere on the board
DVDD: C196.2, C202.2, P3V1.1, U26.1 (VOUT1); also elsewhere on the board
unnamed: R80.1, T1.4 (G)
unnamed: R82.1, R85.2, U20.9 (FB)
unnamed: R83.1, R84.2, U21.9 (FB)
unnamed: R81.1, U21.12 (PGOOD)
unnamed: R87.1, R88.2, U22.9 (FB)
unnamed: R86.1, U22.12 (PGOOD)
unnamed: R90.1, R91.2, U23.4 (FB)
ON_439: JP3.1 (A), R89.2, U24.2 (~SD1); also elsewhere on the board
ON_984: JP3.3 (B), R92.2, U25.2 (~SD1), U25.3 (~SD2), U26.4 (EN2), U26.6 (EN1), U27.4 (EN2); also elsewhere on the board
REF5V: C199.2, C205.2, U28.5 (OUT_S), U28.6 (OUT_F); also elsewhere on the board
VCCPD: C195.2, C201.2, P5V4.1, U25.7 (OUT2); also elsewhere on the board
VDDCP: C194.2, C200.2, P5V3.1, U25.8 (OUT1); also elsewhere on the board
VDDPD: C197.2, C203.2, P3V2.1, U26.2 (VOUT2); also elsewhere on the board

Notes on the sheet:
5V/3mA
3V/6mA
5V/87mA
3V/5mA
3V/24mA

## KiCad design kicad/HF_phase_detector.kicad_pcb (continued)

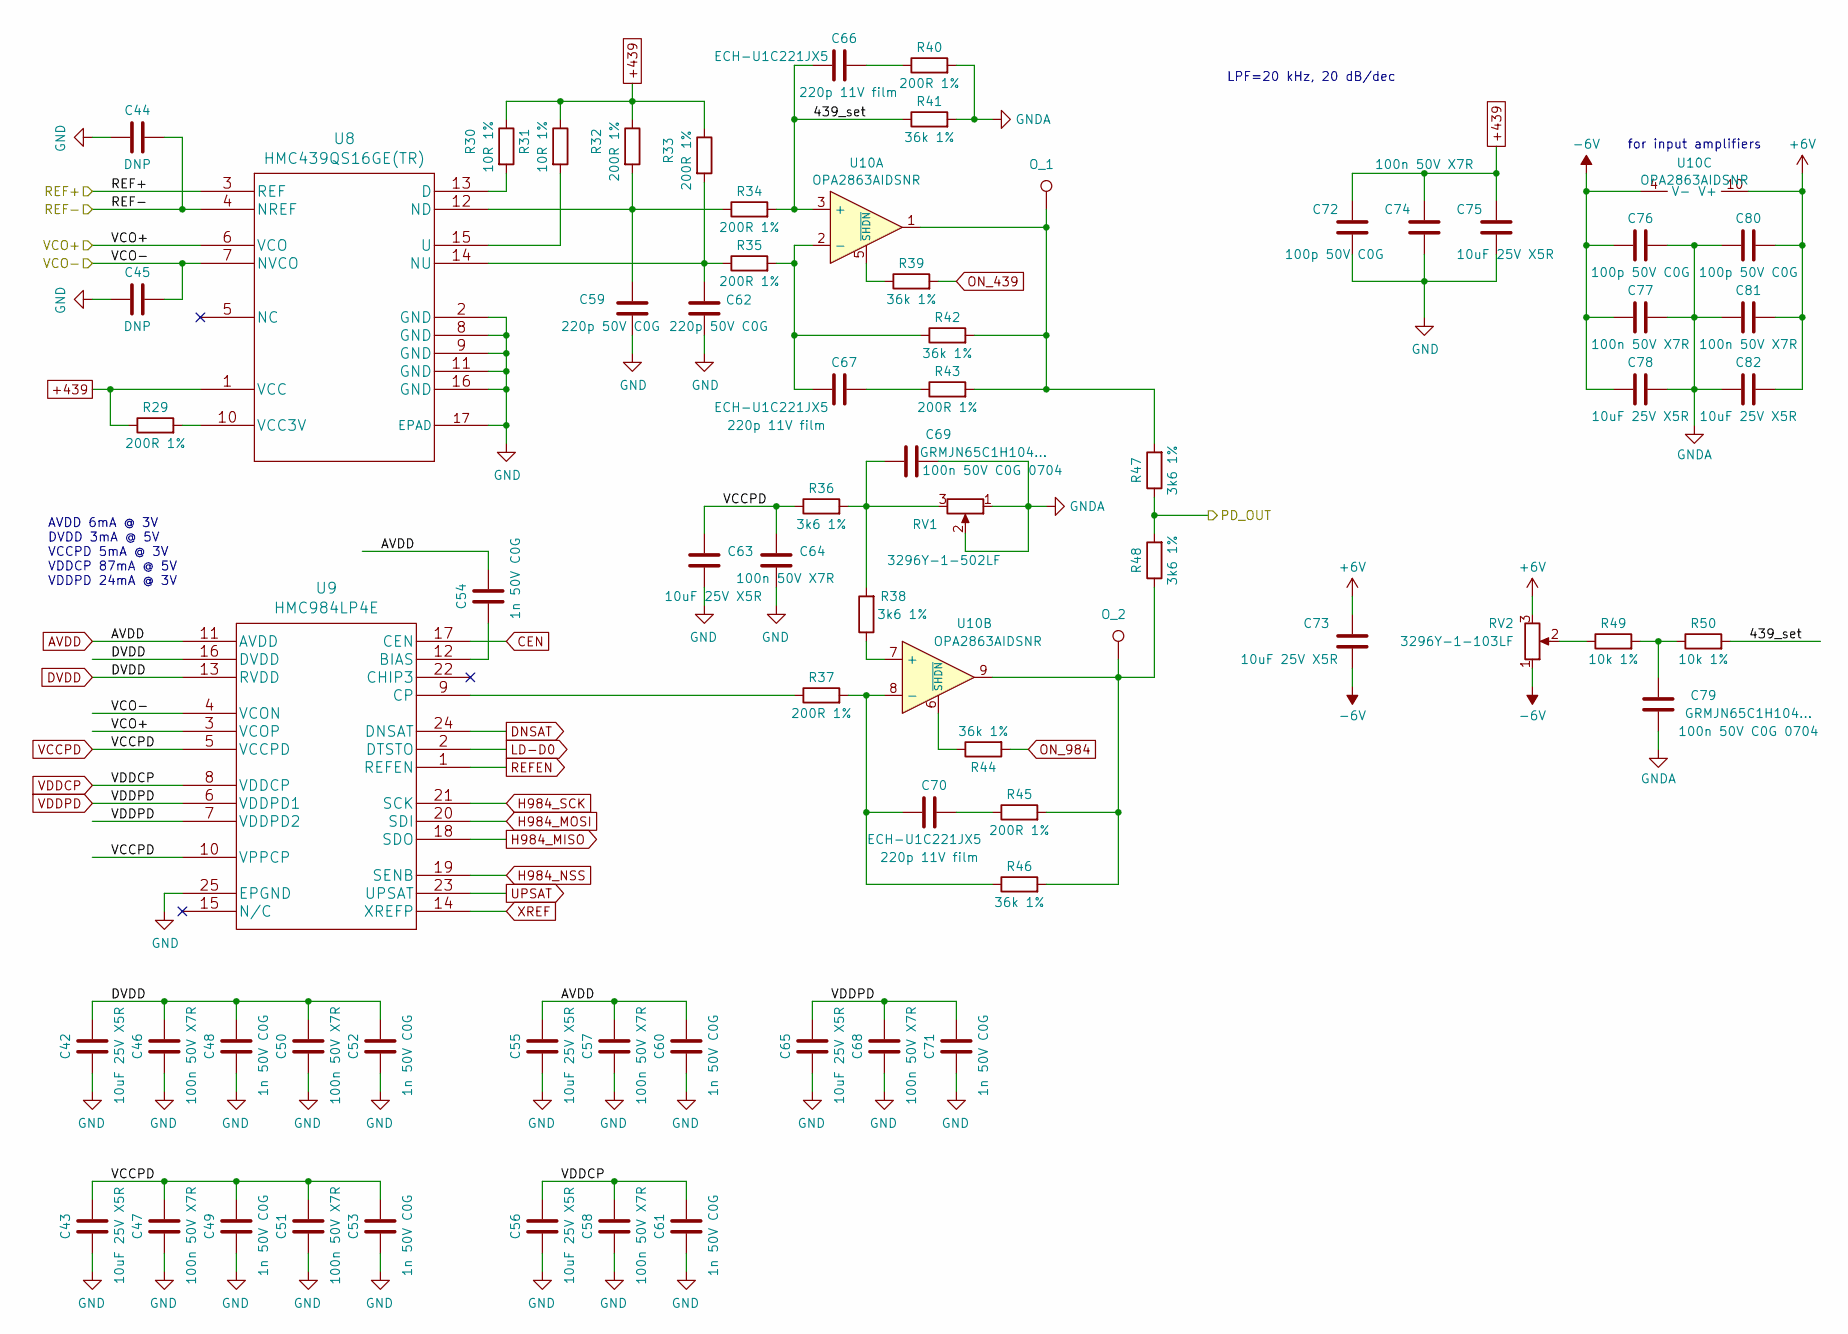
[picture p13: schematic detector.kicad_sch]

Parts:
C42, C43, C55, C56, C63, C65, C73, C75, C78, C82: GRM188R61E106KA73; C_0603_1608Metric
C44, C45: DNP; C_0603_1608Metric
C46, C47, C50, C51, C57, C58, C64, C68, C74, C77, C81: 100n 50V X7R; C_0603_1608Metric
C48, C49, C52, C53, C54, C60, C61, C71: 1n 50V C0G; C_0603_1608Metric
C59, C62: 220p 50V C0G; C_0603_1608Metric
C66, C67, C70: ECH-U1C221JX5; C_0603_1608Metric
C69, C79: GRMJN65C1H104...; C_0805_2012Metric
C72, C76, C80: 100p 50V C0G; C_0603_1608Metric
O_1, O_2: TestPoint; TestPoint_THTPad_1.5x1.5mm_Drill0.7mm
R29: 200R 1%; R_0805_2012Metric
R30, R31: 10R 1%; R_0603_1608Metric
R32, R33, R34, R35, R37, R40, R43, R45: 200R 1%; R_0603_1608Metric
R36, R38, R47, R48: 3k6 1%; R_0603_1608Metric
R39, R41, R42, R44, R46: 36k 1%; R_0603_1608Metric
R49, R50: 10k 1%; R_0603_1608Metric
RV1: 3296Y-1-502LF; Potentiometer_Bourns_3296Y_Vertical
RV2: 3296Y-1-103LF; Potentiometer_Bourns_3296Y_Vertical
U8: HMC439QS16GE(TR); QS16GE_ADI
U9: HMC984LP4E; QFN-24-1EP_4x4mm_P0.5mm_EP2.15x2.15mm_ThermalVias
U10: OPA2863AIDSNR; DFN-10-1EP_3x3mm_P0.5mm_EP1.65x2.38mm_ThermalVias

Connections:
/DIV14-: C44.1, U8.4 (NREF); also elsewhere on the board
/DIV24+: U8.6 (VCO), U9.3 (VCOP); also elsewhere on the board
/DIV24-: C45.1, U8.7 (NVCO), U9.4 (VCON); also elsewhere on the board
/PI and outputs/PD_OUT_set: R47.1, R48.2; also elsewhere on the board
/Phase detector/439_set: C66.1, R34.2, R41.1, R50.2, U10.3 (+)
AVDD: C54.2, C55.2, C57.1, C60.1, U9.11 (AVDD); also elsewhere on the board
CEN: U9.17 (CEN); also elsewhere on the board
DNSAT: U9.24 (DNSAT); also elsewhere on the board
DVDD: C42.2, C46.1, C48.1, C50.1, C52.1, U9.13 (RVDD), U9.16 (DVDD); also elsewhere on the board
H984_MISO: U9.18 (SDO); also elsewhere on the board
H984_MOSI: U9.20 (SDI); also elsewhere on the board
H984_NSS: U9.19 (SENB); also elsewhere on the board
H984_SCK: U9.21 (SCK); also elsewhere on the board
LD-D0: U9.2 (DTSTO); also elsewhere on the board
unnamed: C66.2, R40.1
unnamed: C67.2, R43.1
unnamed: C69.1, R36.2, R38.2, RV1.3
unnamed: C70.2, R45.1
unnamed: C79.1, R49.2, R50.1
unnamed: O_1.1, R42.2, R43.2, R47.2, U10.1
unnamed: O_2.1, R45.2, R46.2, R48.1, U10.9
unnamed: R49.1, RV2.2
unnamed: R30.2, U8.13 (D)
unnamed: C59.2, R32.2, R34.1, U8.12 (ND)
unnamed: C62.2, R33.2, R35.1, U8.14 (NU)
unnamed: R31.2, U8.15 (U)
unnamed: R29.2, U8.10 (VCC3V)
unnamed: C54.1, U9.12 (BIAS)
unnamed: R37.1, U9.9 (CP)
unnamed: C67.1, R35.2, R42.1, U10.2 (-)
unnamed: R39.1, U10.5 (~SHDN)
unnamed: R38.1, U10.7 (+)
unnamed: C70.1, R37.2, R46.1, U10.8 (-)
unnamed: R44.1, U10.6 (~SHDN)
ON_439: R39.2; also elsewhere on the board
ON_984: R44.2; also elsewhere on the board
REFEN: U9.1 (REFEN); also elsewhere on the board
UPSAT: U9.23 (UPSAT); also elsewhere on the board
VCCPD: C43.2, C47.1, C49.1, C51.1, C53.1, C63.2, C64.1, R36.1, U9.5 (VCCPD), U9.10 (VPPCP); also elsewhere on the board
VDDCP: C56.2, C58.1, C61.1, U9.8 (VDDCP); also elsewhere on the board
VDDPD: C65.2, C68.1, C71.1, U9.6 (VDDPD1), U9.7 (VDDPD2); also elsewhere on the board
XREF: U9.14 (XREFP); also elsewhere on the board

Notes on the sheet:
AVDD 6mA @ 3V DVDD 3mA @ 5V VCCPD 5mA @ 3V VDDCP 87mA @ 5V VDDPD 24mA @ 3V
for input amplifiers
LPF=20 kHz, 20 dB/dec

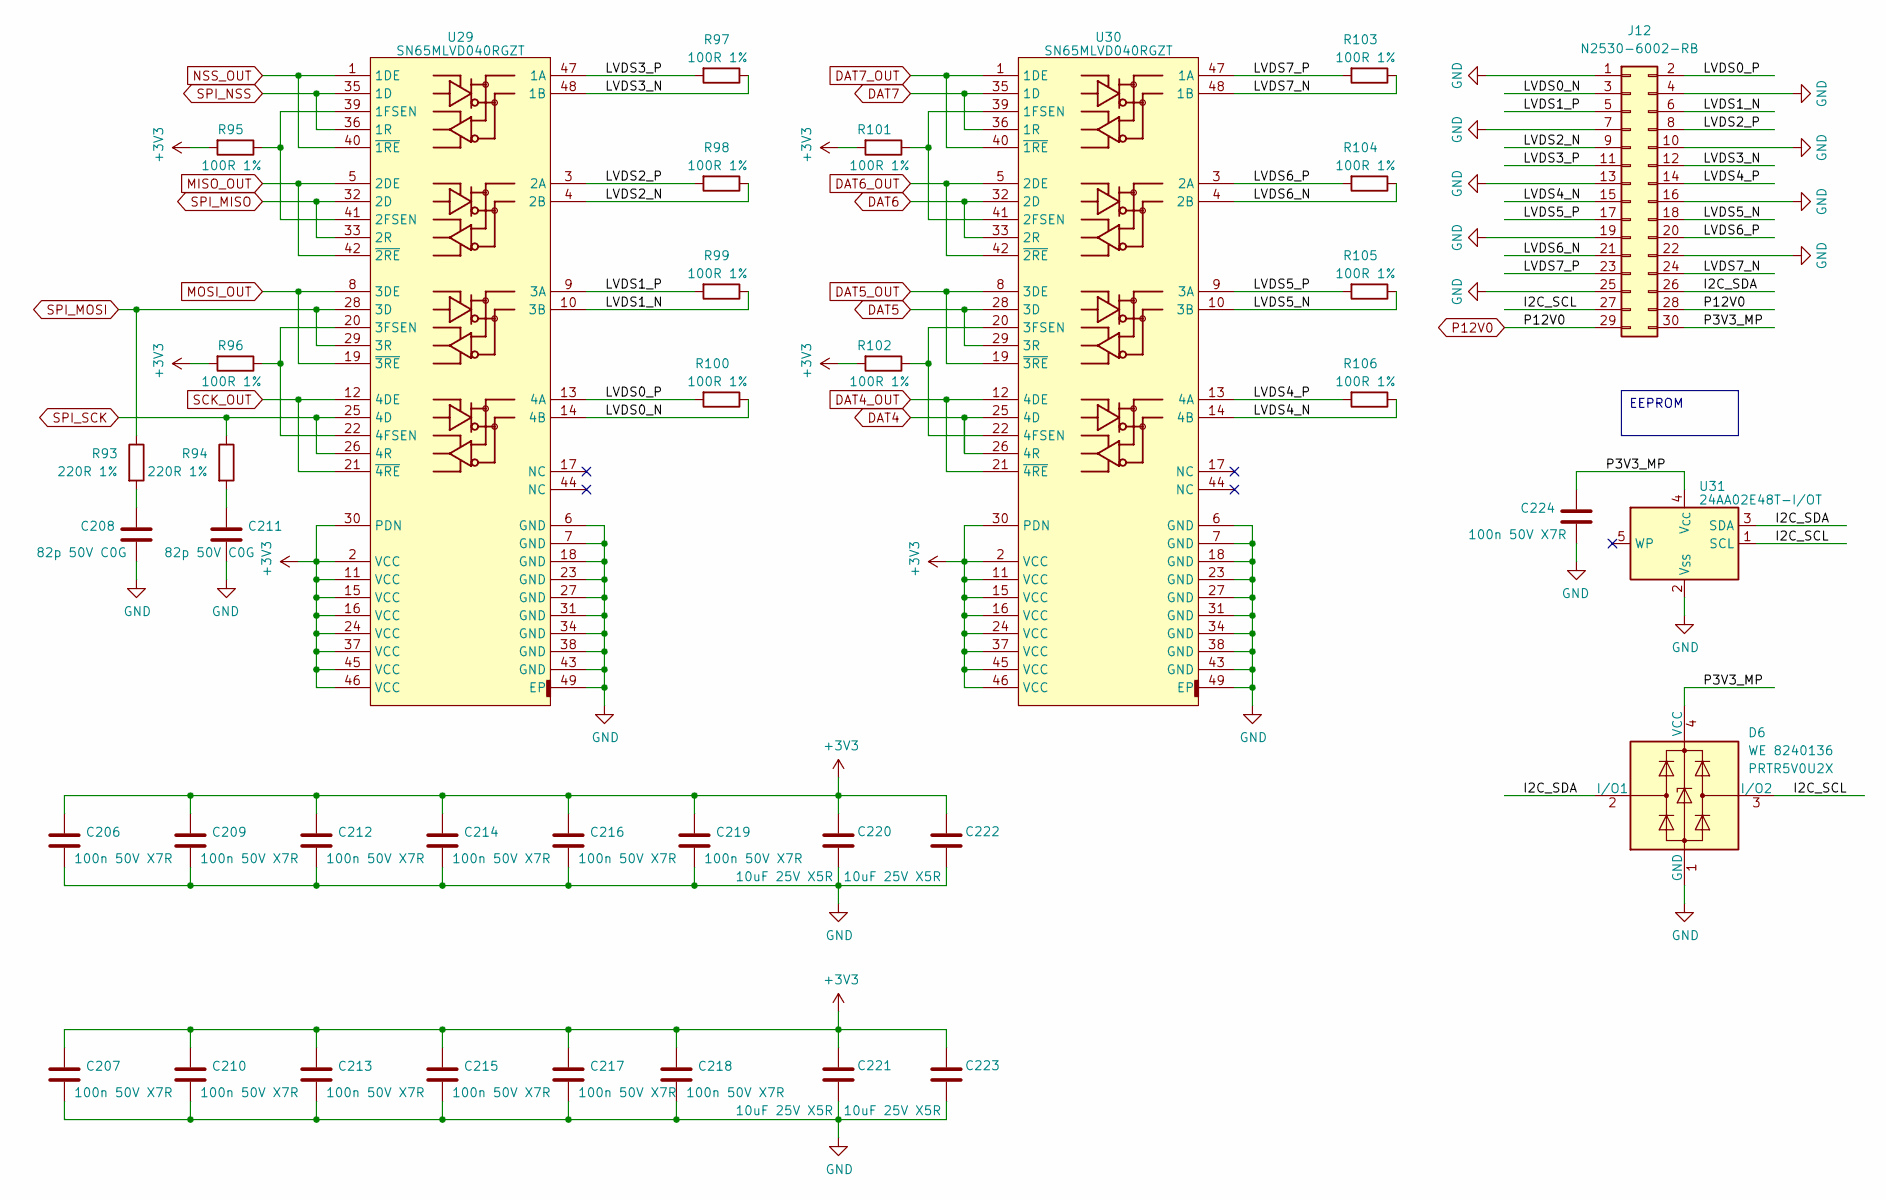
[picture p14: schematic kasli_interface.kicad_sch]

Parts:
C206, C207, C209, C210, C212, C213, C214, C215, C216, C217, C218, C219, C224: 100n 50V X7R; C_0603_1608Metric
C208, C211: 82p 50V C0G; C_0603_1608Metric
C220, C221, C222, C223: GRM188R61E106KA73; C_0603_1608Metric
D6: WE 8240136; SOT-143
J12: N2530-6002-RB; IDC-Header_2x15_P2.54mm_Vertical
R93, R94: 220R 1%; R_0603_1608Metric
R95, R96, R97, R98, R99, R100, R101, R102, R103, R104, R105, R106: 100R 1%; R_0603_1608Metric
U29, U30: SN65MLVD040RGZT; VQFN-48-1EP_7x7mm_P0.5mm_EP4.1x4.1mm_ThermalVias
U31: 24AA02E48T-I/OT; SOT-23-5

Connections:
/Kasli interface1/I2C_SCL: D6.3 (I/O2), J12.27, U31.1 (SCL)
/Kasli interface1/I2C_SDA: D6.2 (I/O1), J12.26, U31.3 (SDA)
/Kasli interface1/LVDS0_N: J12.3, R100.1, U29.14 (4B)
/Kasli interface1/LVDS0_P: J12.2, R100.2, U29.13 (4A)
/Kasli interface1/LVDS1_N: J12.6, R99.1, U29.10 (3B)
/Kasli interface1/LVDS1_P: J12.5, R99.2, U29.9 (3A)
/Kasli interface1/LVDS2_N: J12.9, R98.1, U29.4 (2B)
/Kasli interface1/LVDS2_P: J12.8, R98.2, U29.3 (2A)
/Kasli interface1/LVDS3_N: J12.12, R97.1, U29.48 (1B)
/Kasli interface1/LVDS3_P: J12.11, R97.2, U29.47 (1A)
/Kasli interface1/LVDS4_N: J12.15, R106.1, U30.14 (4B)
/Kasli interface1/LVDS4_P: J12.14, R106.2, U30.13 (4A)
/Kasli interface1/LVDS5_N: J12.18, R105.1, U30.10 (3B)
/Kasli interface1/LVDS5_P: J12.17, R105.2, U30.9 (3A)
/Kasli interface1/LVDS6_N: J12.21, R104.1, U30.4 (2B)
/Kasli interface1/LVDS6_P: J12.20, R104.2, U30.3 (2A)
/Kasli interface1/LVDS7_N: J12.24, R103.1, U30.48 (1B)
/Kasli interface1/LVDS7_P: J12.23, R103.2, U30.47 (1A)
/Kasli interface1/P3V3_MP: C224.1, D6.4 (VCC), J12.30, U31.4 (V_{CC})
DAT4: U30.25 (4D), U30.26 (4R); also elsewhere on the board
DAT4_OUT: U30.12 (4DE), U30.21 (~4RE); also elsewhere on the board
DAT5: U30.28 (3D), U30.29 (3R); also elsewhere on the board
DAT5_OUT: U30.8 (3DE), U30.19 (~3RE); also elsewhere on the board
DAT6: U30.32 (2D), U30.33 (2R); also elsewhere on the board
DAT6_OUT: U30.5 (2DE), U30.42 (~2RE); also elsewhere on the board
DAT7: U30.35 (1D), U30.36 (1R); also elsewhere on the board
DAT7_OUT: U30.1 (1DE), U30.40 (~1RE); also elsewhere on the board
MISO_OUT: U29.5 (2DE), U29.42 (~2RE); also elsewhere on the board
MOSI_OUT: U29.8 (3DE), U29.19 (~3RE); also elsewhere on the board
NSS_OUT: U29.1 (1DE), U29.40 (~1RE); also elsewhere on the board
unnamed: C208.1, R93.2
unnamed: C211.1, R94.2
unnamed: R95.1, U29.39 (1FSEN), U29.41 (2FSEN)
unnamed: R96.1, U29.20 (3FSEN), U29.22 (4FSEN)
unnamed: R101.1, U30.39 (1FSEN), U30.41 (2FSEN)
unnamed: R102.1, U30.20 (3FSEN), U30.22 (4FSEN)
SCK_OUT: U29.12 (4DE), U29.21 (~4RE); also elsewhere on the board
SPI_MISO: U29.32 (2D), U29.33 (2R); also elsewhere on the board
SPI_MOSI: R93.1, U29.28 (3D), U29.29 (3R); also elsewhere on the board
SPI_NSS: U29.35 (1D), U29.36 (1R); also elsewhere on the board
SPI_SCK: R94.1, U29.25 (4D), U29.26 (4R); also elsewhere on the board

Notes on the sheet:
EEPROM

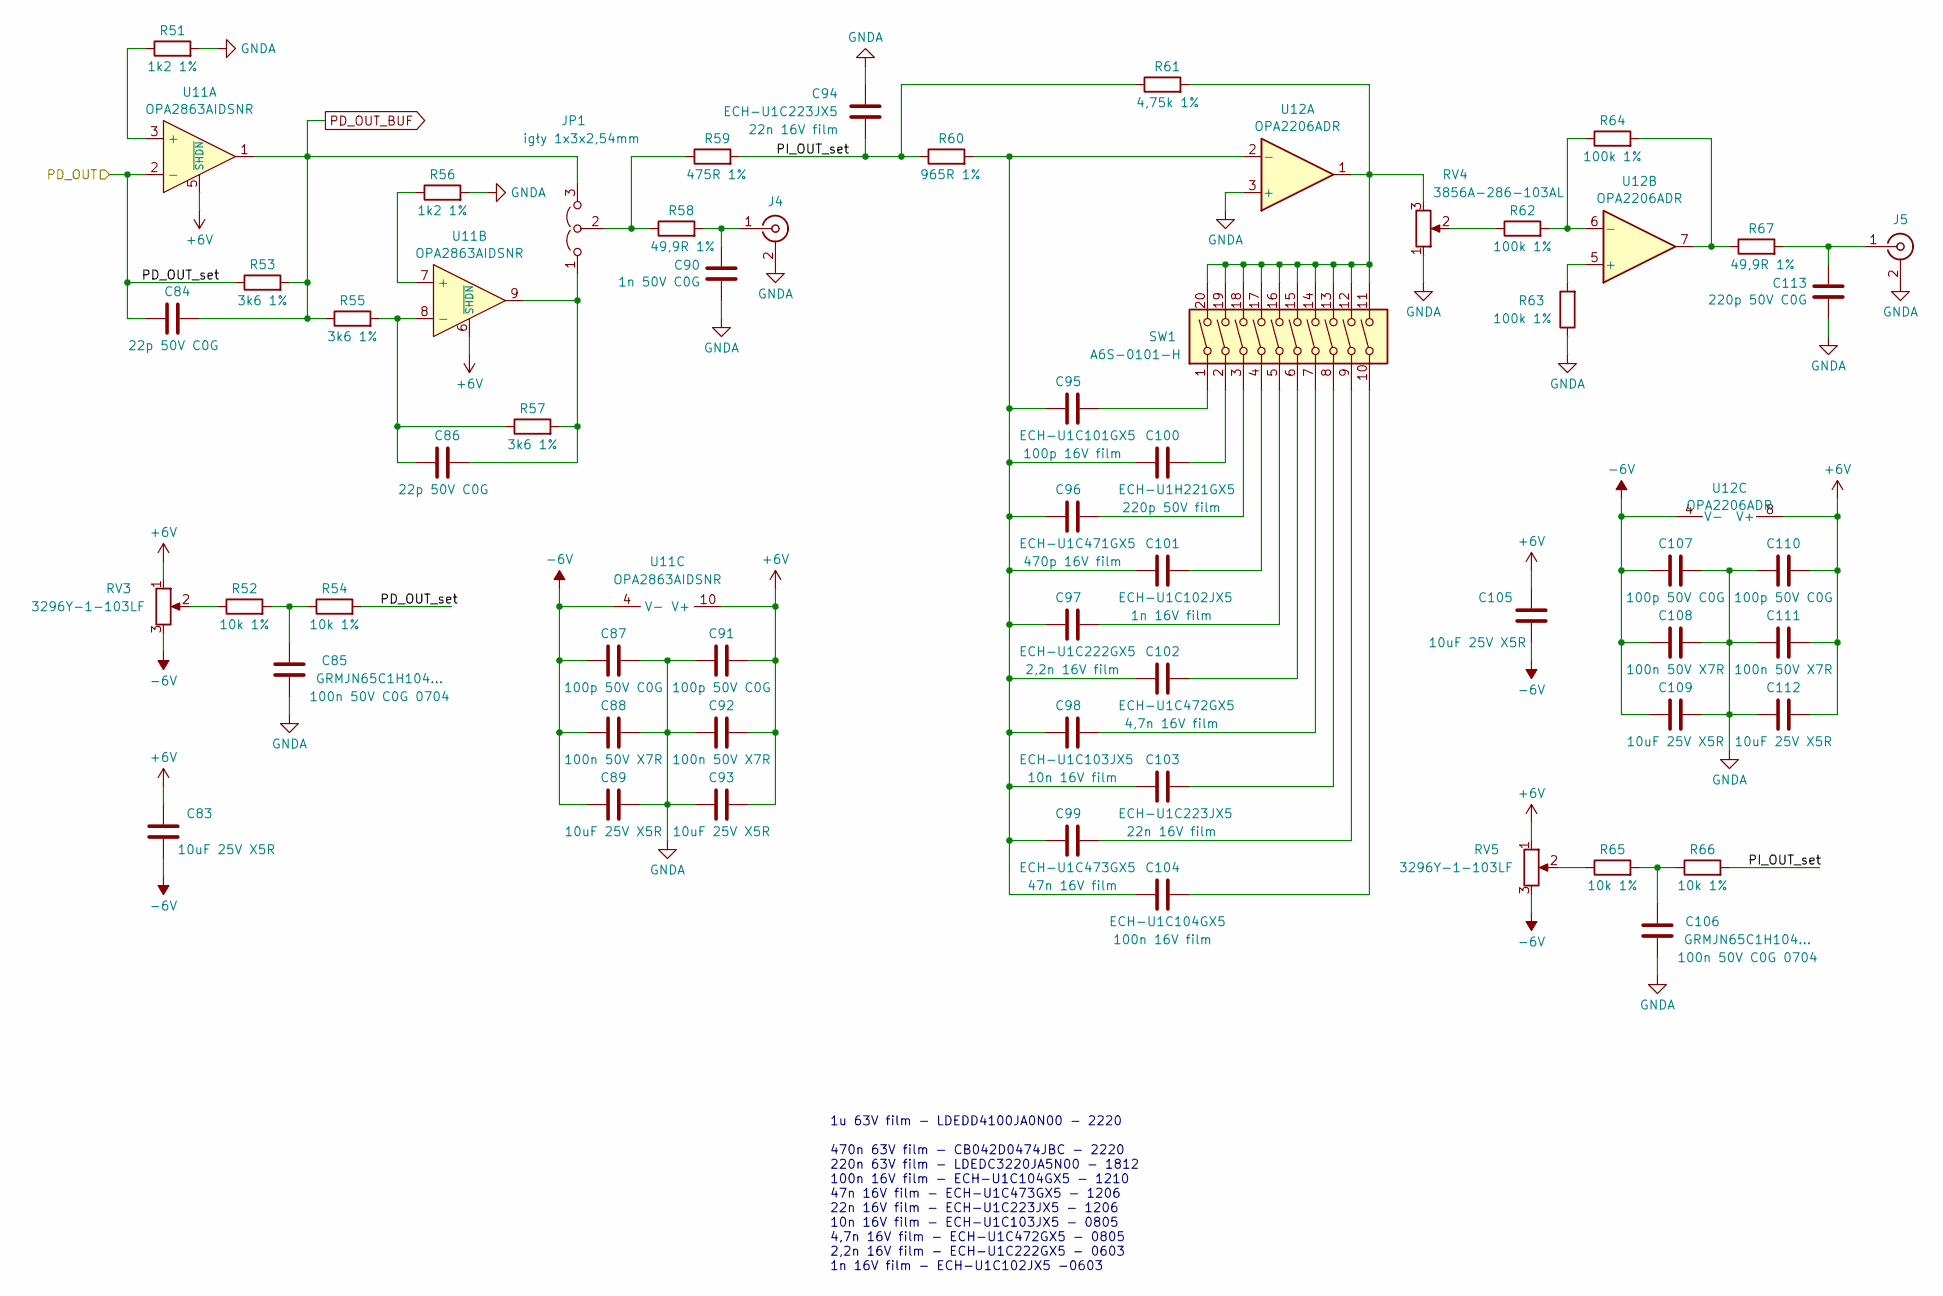
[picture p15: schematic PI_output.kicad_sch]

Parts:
C83, C89, C93, C105, C109, C112: GRM188R61E106KA73; C_0603_1608Metric
C84, C86: 22p 50V C0G; C_0603_1608Metric
C85, C106: GRMJN65C1H104...; C_0805_2012Metric
C87, C91, C107, C110: 100p 50V C0G; C_0603_1608Metric
C88, C92, C108, C111: 100n 50V X7R; C_0603_1608Metric
C90: 1n 50V C0G; C_0603_1608Metric
C94, C103: ECH-U1C223JX5; C_1206_3216Metric
C95: ECH-U1C101GX5; C_0603_1608Metric
C96: ECH-U1C471GX5; C_0603_1608Metric
C97: ECH-U1C222GX5; C_0603_1608Metric
C98: ECH-U1C103JX5; C_0805_2012Metric
C99: ECH-U1C473GX5; C_1206_3216Metric
C100: ECH-U1H221GX5; C_0805_2012Metric
C101: ECH-U1C102JX5; C_0603_1608Metric
C102: ECH-U1C472GX5; C_0805_2012Metric
C104: ECH-U1C104GX5; C_1210_3225Metric
C113: 220p 50V C0G; C_0603_1608Metric
J4, J5: RF2-49B-T-00-50-G-HDW; SMA_Amphenol_132203-12_Horizontal
JP1: igły 1x3x2,54mm; PinHeader_1x03_P2.54mm_Vertical
R51, R56: 1k2 1%; R_0603_1608Metric
R52, R54, R65, R66: 10k 1%; R_0603_1608Metric
R53, R55, R57: 3k6 1%; R_0603_1608Metric
R58, R67: 49,9R 1%; R_0603_1608Metric
R59: 475R 1%; R_0603_1608Metric
R60: 965R 1%; R_0603_1608Metric
R61: 4,75k 1%; R_0603_1608Metric
R62, R63, R64: 100k 1%; R_0603_1608Metric
RV3, RV5: 3296Y-1-103LF; Potentiometer_Bourns_3296Y_Vertical
RV4: 3856A-286-103AL; Potentiometer_Bourns_3856A-286_horizontal
SW1: A6S-0101-H; SW_DIP_SPSTx10_Slide_9.78x27.58mm_W8.61mm_P2.54mm
U11: OPA2863AIDSNR; DFN-10-1EP_3x3mm_P0.5mm_EP1.65x2.38mm_ThermalVias
U12: OPA2206ADR; SOIC-8_3.9x4.9mm_P1.27mm

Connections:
/PI and outputs/PD_OUT_set: C84.1, R53.1, R54.2, U11.2 (-); also elsewhere on the board
/PI and outputs/PI_OUT_set: C94.1, R59.2, R60.1, R61.1, R66.2
unnamed: C85.1, R52.2, R54.1
unnamed: C95.2, SW1.1
unnamed: C96.2, SW1.3
unnamed: C97.2, SW1.5
unnamed: C98.2, SW1.7
unnamed: C99.2, SW1.9
unnamed: C100.2, SW1.2
unnamed: C101.2, SW1.4
unnamed: C102.2, SW1.6
unnamed: C103.2, SW1.8
unnamed: C104.2, SW1.10
unnamed: C106.1, R65.2, R66.1
unnamed: C90.2, J4.1 (In), R58.2
unnamed: C113.2, J5.1 (In), R67.2
unnamed: C86.2, JP1.1 (A), R57.2, U11.9
unnamed: JP1.2 (C), R58.1, R59.1
unnamed: R52.1, RV3.2
unnamed: R61.2, RV4.3, SW1.11, SW1.12, SW1.13, SW1.14, SW1.15, SW1.16, SW1.17, SW1.18, SW1.19, SW1.20, U12.1
unnamed: R62.1, RV4.2
unnamed: R64.2, R67.1, U12.7
unnamed: R65.1, RV5.2
unnamed: R51.1, U11.3 (+)
unnamed: R56.1, U11.7 (+)
unnamed: C86.1, R55.2, R57.1, U11.8 (-)
unnamed: C95.1, C96.1, C97.1, C98.1, C99.1, C100.1, C101.1, C102.1, C103.1, C104.1, R60.2, U12.2 (-)
unnamed: R63.2, U12.5 (+)
unnamed: R62.2, R64.1, U12.6 (-)
PD_OUT_BUF: C84.2, JP1.3 (B), R53.2, R55.1, U11.1; also elsewhere on the board

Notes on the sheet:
1u 63V film - LDEDD4100JA0N00 - 2220 470n 63V film - CB042D0474JBC - 2220 220n 63V film - LDEDC3220JA5N00 - 1812 100n 16V film - ECH-U1C104GX5 - 1210 47n 16V film - ECH-U1C473GX5 - 1206 22n 16V film - ECH-U1C223JX5 - 1206 10n 16V film - ECH-U1C103JX5 - 0805 4,7n 16V film - ECH-U1C472GX5 - 0805 2,2n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

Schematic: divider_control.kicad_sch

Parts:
C38: 1n 50V C0G; C_0603_1608Metric
C39: 100p 50V C0G; C_0603_1608Metric
C40: 100n 50V X7R; C_0603_1608Metric
C41: GRM188R61E106KA73; C_0603_1608Metric
D3: BAT54SW...; SOT-323_SC-70
J3: RF2-49B-T-00-50-G-HDW; SMA_Amphenol_132203-12_Horizontal
R23: 49,9R 1%; R_0603_1608Metric
R24, R25: 680R 1%; R_0603_1608Metric
R26, R27: 60,4k 1%; R_0603_1608Metric
R28: 150k 1%; R_0603_1608Metric
U6: TBD62003AFNG,EL; SSOP-16_4.4x5.2mm_P0.65mm
U7: TLV3603DCKx; SOT-363_SC-70-6

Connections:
10MHz_in: U7.1; also elsewhere on the board
/Inputs and prescalers/DIV1_S0: U6.12 (O5); also elsewhere on the board
/Inputs and prescalers/DIV1_S1: U6.11 (O6); also elsewhere on the board
/Inputs and prescalers/DIV1_S2: R27.1; also elsewhere on the board
/Inputs and prescalers/DIV2_S0: U6.16 (O1); also elsewhere on the board
/Inputs and prescalers/DIV2_S1: U6.15 (O2); also elsewhere on the board
/Inputs and prescalers/DIV2_S2: R26.1; also elsewhere on the board
unnamed: C38.1, R23.1, R24.2
unnamed: D3.3 (COM), R24.1, U7.3 (+)
unnamed: C38.2, J3.1 (In)
unnamed: R26.2, U6.14 (O3)
unnamed: R27.2, U6.10 (O7)
unnamed: R25.1, U7.4 (-)
unnamed: R28.1, U7.5 (~LE)
iDIV1_S0: U6.5 (I5); also elsewhere on the board
iDIV1_S1: U6.6 (I6); also elsewhere on the board
iDIV1_S2: U6.7 (I7); also elsewhere on the board
iDIV2_S0: U6.1 (I1); also elsewhere on the board
iDIV2_S1: U6.2 (I2); also elsewhere on the board
iDIV2_S2: U6.3 (I3); also elsewhere on the board

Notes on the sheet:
degree of division iDIVx_S0 iDIVx_S1 iDIVx_S2 1 H H H 2 L H H 4 H H L 8 H L L 16 L L L see page 4-5 of https://www.ti.com/lit/ds/symlink/cdcm1804.pdf
10 MHz input

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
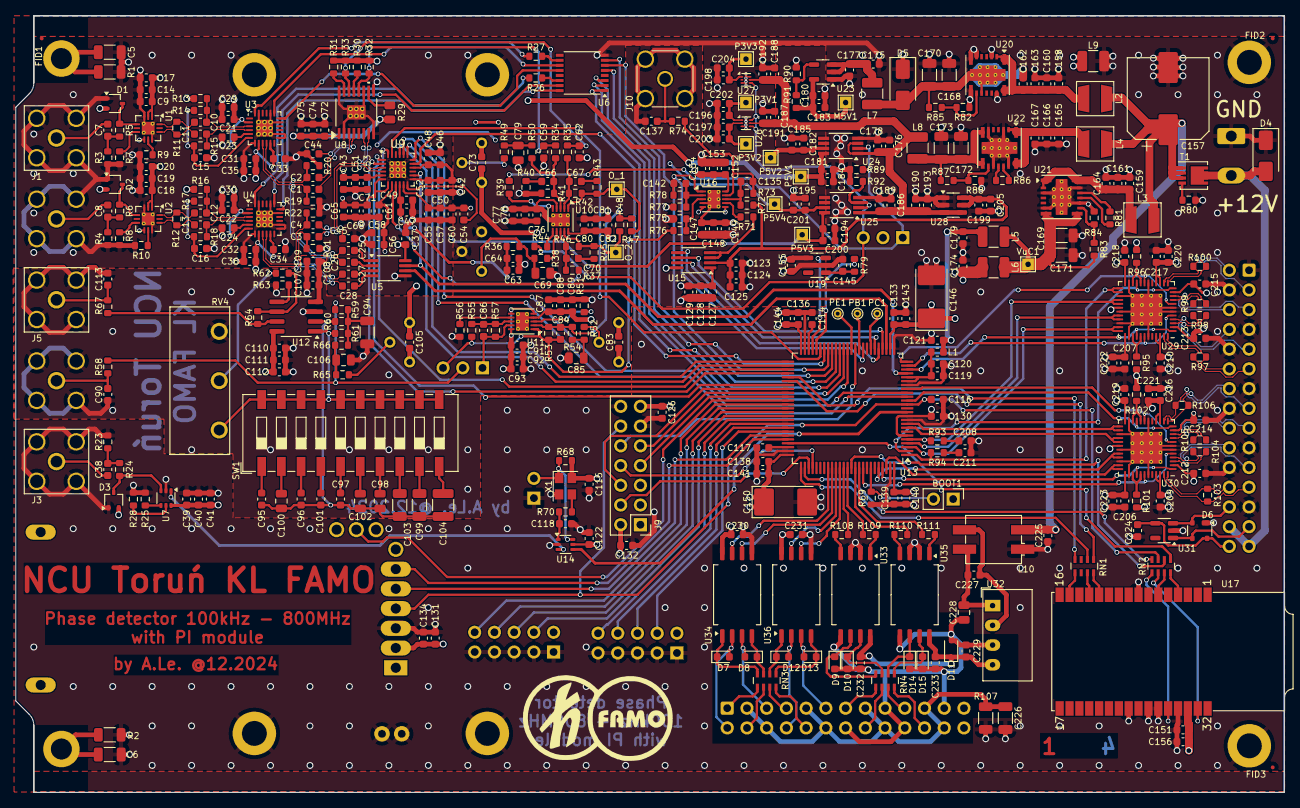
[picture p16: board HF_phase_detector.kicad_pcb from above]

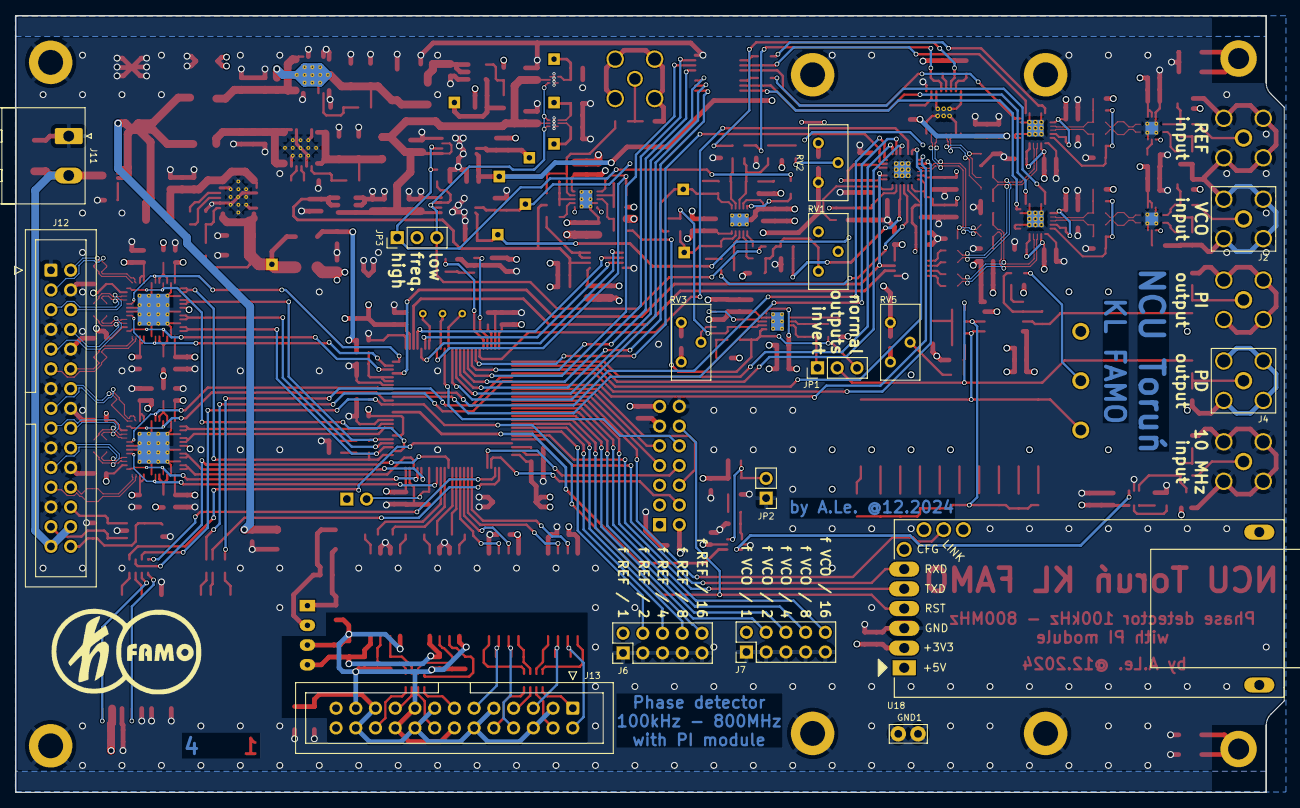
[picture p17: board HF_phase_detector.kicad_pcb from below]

Board: 4 copper layers, 163.3 x 100.0 mm, 461 parts (17 on the bottom side), 284 nets.

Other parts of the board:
C157: AEA1010471M025R; CP_Elec_10x10
C167, C178, C182: 100n 50V X7R; C_0603_1608Metric
C173: GRM31CR61A476KE15L; C_1206_3216Metric
J11: MSTBA 2,5/ 2-G-5,08 1757242; PhoenixContact_MSTBA_2,5_2-G-5,08_1x02_P5.08mm_Horizontal
L4: LQH44NN101K03L; L_MURATA_LQH44
L8: LQH32PN100MNCL; L_1210_3225Metric
P5V2: TestPoint; TestPoint_THTPad_1.5x1.5mm_Drill0.7mm

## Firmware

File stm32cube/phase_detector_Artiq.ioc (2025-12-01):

#MicroXplorer Configuration settings - do not modify
CAD.formats=
CAD.pinconfig=
CAD.provider=
CORTEX_M7.CPU_DCache=Disabled
CORTEX_M7.CPU_ICache=Disabled
CORTEX_M7.IPParameters=default_mode_Activation,CPU_ICache,CPU_DCache,MPU_Control
CORTEX_M7.MPU_Control=__NULL
CORTEX_M7.default_mode_Activation=0
File.Version=6
GPIO.groupedBy=Group By Peripherals
KeepUserPlacement=false
MMTAppRegionsCount=0
MMTConfigApplied=false
Mcu.CPN=STM32H743VIT6
Mcu.Family=STM32H7
Mcu.IP0=CORTEX_M7
Mcu.IP1=DEBUG
Mcu.IP10=UART4
Mcu.IP11=USART1
Mcu.IP12=USART3
Mcu.IP13=USART6
Mcu.IP2=MEMORYMAP
Mcu.IP3=NVIC
Mcu.IP4=RCC
Mcu.IP5=SPI2
Mcu.IP6=SYS
Mcu.IP7=TIM2
Mcu.IP8=TIM5
Mcu.IP9=TIM6
Mcu.IPNb=14
Mcu.Name=STM32H743VITx
Mcu.Package=LQFP100
Mcu.Pin0=PH0-OSC_IN (PH0)
Mcu.Pin1=PH1-OSC_OUT (PH1)
Mcu.Pin10=PE12
Mcu.Pin11=PE13
Mcu.Pin12=PE14
Mcu.Pin13=PB12
Mcu.Pin14=PB13
Mcu.Pin15=PD8
Mcu.Pin16=PD9
Mcu.Pin17=PC6
Mcu.Pin18=PC7
Mcu.Pin19=PA9
Mcu.Pin2=PC1
Mcu.Pin20=PA10
Mcu.Pin21=PA11
Mcu.Pin22=PA12
Mcu.Pin23=PA13 (JTMS/SWDIO)
Mcu.Pin24=PA14 (JTCK/SWCLK)
Mcu.Pin25=PA15 (JTDI)
Mcu.Pin26=PB3 (JTDO/TRACESWO)
Mcu.Pin27=VP_SYS_VS_Systick
Mcu.Pin28=VP_TIM6_VS_ClockSourceINT
Mcu.Pin29=VP_MEMORYMAP_VS_MEMORYMAP
Mcu.Pin3=PC2_C
Mcu.Pin4=PA0
Mcu.Pin5=PA4
Mcu.Pin6=PE8
Mcu.Pin7=PE9
Mcu.Pin8=PE10
Mcu.Pin9=PE11
Mcu.PinsNb=30
Mcu.ThirdPartyNb=0
Mcu.UserConstants=
Mcu.UserName=STM32H743VITx
MxCube.Version=6.12.0
MxDb.Version=DB.6.0.120
NVIC.BusFault_IRQn=true\:0\:0\:false\:false\:true\:false\:false\:false
NVIC.DebugMonitor_IRQn=true\:0\:0\:false\:false\:true\:false\:false\:false
NVIC.ForceEnableDMAVector=true
NVIC.HardFault_IRQn=true\:0\:0\:false\:false\:true\:false\:false\:false
NVIC.MemoryManagement_IRQn=true\:0\:0\:false\:false\:true\:false\:false\:false
NVIC.NonMaskableInt_IRQn=true\:0\:0\:false\:false\:true\:false\:false\:false
NVIC.PendSV_IRQn=true\:0\:0\:false\:false\:true\:false\:false\:false
NVIC.PriorityGroup=NVIC_PRIORITYGROUP_4
NVIC.SVCall_IRQn=true\:0\:0\:false\:false\:true\:false\:false\:false
NVIC.SysTick_IRQn=true\:15\:0\:false\:false\:true\:false\:true\:false
NVIC.TIM6_DAC_IRQn=true\:0\:0\:false\:false\:true\:true\:true\:true
NVIC.UsageFault_IRQn=true\:0\:0\:false\:false\:true\:false\:false\:false
PA0.GPIOParameters=GPIO_Speed,GPIO_Label
PA0.GPIO_Label=XREF
PA0.GPIO_Speed=GPIO_SPEED_FREQ_VERY_HIGH
PA0.Locked=true
PA0.Signal=S_TIM2_CH1_ETR
PA10.GPIOParameters=GPIO_Label
PA10.GPIO_Label=RXD1
PA10.Locked=true
PA10.Mode=Asynchronous
PA10.Signal=USART1_RX
PA11.Locked=true
PA11.Mode=Asynchronous
PA11.Signal=UART4_RX
PA12.Locked=true
PA12.Mode=Asynchronous
PA12.Signal=UART4_TX
PA13\ (JTMS/SWDIO).Mode=JTAG_4_pins
PA13\ (JTMS/SWDIO).Signal=DEBUG_JTMS-SWDIO
PA14\ (JTCK/SWCLK).Mode=JTAG_4_pins
PA14\ (JTCK/SWCLK).Signal=DEBUG_JTCK-SWCLK
PA15\ (JTDI).Mode=JTAG_4_pins
PA15\ (JTDI).Signal=DEBUG_JTDI
PA4.GPIOParameters=GPIO_Label
PA4.GPIO_Label=XVCO
PA4.Locked=true
PA4.Signal=S_TIM5_ETR
PA9.GPIOParameters=GPIO_Label
PA9.GPIO_Label=TXD1
PA9.Locked=true
PA9.Mode=Asynchronous
PA9.Signal=USART1_TX
PB12.GPIOParameters=GPIO_Label
PB12.GPIO_Label=PHDET_NSS
PB12.Locked=true
PB12.Signal=GPIO_Output
PB13.GPIOParameters=GPIO_Label
PB13.GPIO_Label=PHDET_SCK
PB13.Locked=true
PB13.Mode=Full_Duplex_Master
PB13.Signal=SPI2_SCK
PB3\ (JTDO/TRACESWO).Mode=JTAG_4_pins
PB3\ (JTDO/TRACESWO).Signal=DEBUG_JTDO-SWO
PC1.GPIOParameters=GPIO_Label
PC1.GPIO_Label=PHDET_MOSI
PC1.Mode=Full_Duplex_Master
PC1.Signal=SPI2_MOSI
PC2_C.GPIOParameters=GPIO_Label
PC2_C.GPIO_Label=PHDET_MISO
PC2_C.Mode=Full_Duplex_Master
PC2_C.Signal=SPI2_MISO
PC6.GPIOParameters=GPIO_Label
PC6.GPIO_Label=TXD2
PC6.Locked=true
PC6.Mode=Asynchronous
PC6.Signal=USART6_TX
PC7.GPIOParameters=GPIO_Label
PC7.GPIO_Label=RXD2
PC7.Locked=true
PC7.Mode=Asynchronous
PC7.Signal=USART6_RX
PD8.GPIOParameters=GPIO_Label
PD8.GPIO_Label=STLINK_RX
PD8.Locked=true
PD8.Mode=Asynchronous
PD8.Signal=USART3_TX
PD9.GPIOParameters=GPIO_Label
PD9.GPIO_Label=STLINK_TX
PD9.Locked=true
PD9.Mode=Asynchronous
PD9.Signal=USART3_RX
PE10.GPIOParameters=PinState,GPIO_PuPd,GPIO_Label
PE10.GPIO_Label=DIV2_S0
PE10.GPIO_PuPd=GPIO_PULLDOWN
PE10.Locked=true
PE10.PinState=GPIO_PIN_SET
PE10.Signal=GPIO_Output
PE11.GPIOParameters=PinState,GPIO_PuPd,GPIO_Label
PE11.GPIO_Label=DIV1_S2
PE11.GPIO_PuPd=GPIO_PULLDOWN
PE11.Locked=true
PE11.PinState=GPIO_PIN_SET
PE11.Signal=GPIO_Output
PE12.GPIOParameters=PinState,GPIO_PuPd,GPIO_Label
PE12.GPIO_Label=DIV1_S1
PE12.GPIO_PuPd=GPIO_PULLDOWN
PE12.Locked=true
PE12.PinState=GPIO_PIN_SET
PE12.Signal=GPIO_Output
PE13.GPIOParameters=PinState,GPIO_PuPd,GPIO_Label
PE13.GPIO_Label=DIV1_S0
PE13.GPIO_PuPd=GPIO_PULLDOWN
PE13.Locked=true
PE13.PinState=GPIO_PIN_SET
PE13.Signal=GPIO_Output
PE14.GPIOParameters=PinState,GPIO_PuPd,GPIO_Label
PE14.GPIO_Label=PHDET_CEN
PE14.GPIO_PuPd=GPIO_PULLUP
PE14.Locked=true
PE14.PinState=GPIO_PIN_SET
PE14.Signal=GPIO_Output
PE8.GPIOParameters=PinState,GPIO_PuPd,GPIO_Label
PE8.GPIO_Label=DIV2_S1
PE8.GPIO_PuPd=GPIO_PULLDOWN
PE8.Locked=true
PE8.PinState=GPIO_PIN_SET
PE8.Signal=GPIO_Output
PE9.GPIOParameters=PinState,GPIO_PuPd,GPIO_Label
PE9.GPIO_Label=DIV2_S2
PE9.GPIO_PuPd=GPIO_PULLDOWN
PE9.Locked=true
PE9.PinState=GPIO_PIN_SET
PE9.Signal=GPIO_Output
PH0-OSC_IN\ (PH0).Locked=true
PH0-OSC_IN\ (PH0).Mode=HSE-External-Oscillator
PH0-OSC_IN\ (PH0).Signal=RCC_OSC_IN
PH1-OSC_OUT\ (PH1).Locked=true
PH1-OSC_OUT\ (PH1).Mode=HSE-External-Oscillator
PH1-OSC_OUT\ (PH1).Signal=RCC_OSC_OUT
PinOutPanel.RotationAngle=0
ProjectManager.AskForMigrate=true
ProjectManager.BackupPrevious=false
ProjectManager.CompilerOptimize=6
ProjectManager.ComputerToolchain=false
ProjectManager.CoupleFile=false
ProjectManager.CustomerFirmwarePackage=
ProjectManager.DefaultFWLocation=true
ProjectManager.DeletePrevious=true
ProjectManager.DeviceId=STM32H743VITx
ProjectManager.FirmwarePackage=STM32Cube FW_H7 V1.11.2
ProjectManager.FreePins=false
ProjectManager.HalAssertFull=false
ProjectManager.HeapSize=0x200
ProjectManager.KeepUserCode=true
ProjectManager.LastFirmware=true
ProjectManager.LibraryCopy=1
ProjectManager.MainLocation=Core/Src
ProjectManager.NoMain=false
ProjectManager.PreviousToolchain=STM32CubeIDE
ProjectManager.ProjectBuild=false
ProjectManager.ProjectFileName=phase_detector_Artiq.ioc
ProjectManager.ProjectName=phase_detector_Artiq
ProjectManager.ProjectStructure=
ProjectManager.RegisterCallBack=
ProjectManager.StackSize=0x400
ProjectManager.TargetToolchain=STM32CubeIDE
ProjectManager.ToolChainLocation=
ProjectManager.UAScriptAfterPath=
ProjectManager.UAScriptBeforePath=
ProjectManager.UnderRoot=true
ProjectManager.functionlistsort=1-SystemClock_Config-RCC-false-HAL-false,2-MX_GPIO_Init-GPIO-false-HAL-true,3-MX_USART3_UART_Init-USART3-false-HAL-true,4-MX_UART4_Init-UART4-false-HAL-true,5-MX_USART1_UART_Init-USART1-false-HAL-true,6-MX_USART6_UART_Init-USART6-false-HAL-true,7-MX_TIM2_Init-TIM2-false-HAL-true,8-MX_TIM6_Init-TIM6-false-HAL-true,9-MX_SPI2_Init-SPI2-false-HAL-true,0-MX_CORTEX_M7_Init-CORTEX_M7-false-HAL-true
RCC.ADCFreq_Value=90000000
RCC.AHB12Freq_Value=75000000
RCC.AHB4Freq_Value=75000000
RCC.APB1Freq_Value=18750000
RCC.APB2Freq_Value=18750000
RCC.APB3Freq_Value=37500000
RCC.APB4Freq_Value=37500000
RCC.AXIClockFreq_Value=75000000
RCC.CECFreq_Value=32000
RCC.CKPERFreq_Value=32000000
RCC.CortexFreq_Value=75000000
RCC.CpuClockFreq_Value=75000000
RCC.D1CPREFreq_Value=75000000
RCC.D1PPRE=RCC_APB3_DIV2
RCC.D2PPRE1=RCC_APB1_DIV4
RCC.D2PPRE2=RCC_APB2_DIV4
RCC.D3PPRE=RCC_APB4_DIV2
RCC.DFSDMACLkFreq_Value=50000000
RCC.DFSDMFreq_Value=18750000
RCC.DIVM1=4
RCC.DIVM2=1
RCC.DIVN1=60
RCC.DIVN2=18
RCC.DIVP1Freq_Value=75000000
RCC.DIVP2Freq_Value=90000000
RCC.DIVP3Freq_Value=20156250
RCC.DIVQ1=3
RCC.DIVQ1Freq_Value=50000000
RCC.DIVQ2Freq_Value=90000000
RCC.DIVQ3Freq_Value=20156250
RCC.DIVR1Freq_Value=75000000
RCC.DIVR2Freq_Value=90000000
RCC.DIVR3Freq_Value=20156250
RCC.FDCANFreq_Value=50000000
RCC.FMCFreq_Value=75000000
RCC.FamilyName=M
RCC.HCLK3ClockFreq_Value=75000000
RCC.HCLKFreq_Value=75000000
RCC.HRTIMFreq_Value=37500000
RCC.HSE_VALUE=10000000
RCC.HSIDiv=RCC_PLLSAIDIVR_2
RCC.I2C123Freq_Value=18750000
RCC.I2C4Freq_Value=37500000
RCC.IPParameters=ADCFreq_Value,AHB12Freq_Value,AHB4Freq_Value,APB1Freq_Value,APB2Freq_Value,APB3Freq_Value,APB4Freq_Value,AXIClockFreq_Value,CECFreq_Value,CKPERFreq_Value,CortexFreq_Value,CpuClockFreq_Value,D1CPREFreq_Value,D1PPRE,D2PPRE1,D2PPRE2,D3PPRE,DFSDMACLkFreq_Value,DFSDMFreq_Value,DIVM1,DIVM2,DIVN1,DIVN2,DIVP1Freq_Value,DIVP2Freq_Value,DIVP3Freq_Value,DIVQ1,DIVQ1Freq_Value,DIVQ2Freq_Value,DIVQ3Freq_Value,DIVR1Freq_Value,DIVR2Freq_Value,DIVR3Freq_Value,FDCANFreq_Value,FMCFreq_Value,FamilyName,HCLK3ClockFreq_Value,HCLKFreq_Value,HRTIMFreq_Value,HSE_VALUE,HSIDiv,I2C123Freq_Value,I2C4Freq_Value,LPTIM1Freq_Value,LPTIM2Freq_Value,LPTIM345Freq_Value,LPUART1Freq_Value,LTDCFreq_Value,MCO1PinFreq_Value,MCO2PinFreq_Value,PLLFRACN,PLLSourceVirtual,QSPIFreq_Value,RNGFreq_Value,RTCFreq_Value,SAI1Freq_Value,SAI23Freq_Value,SAI4AFreq_Value,SAI4BFreq_Value,SDMMCFreq_Value,SPDIFRXFreq_Value,SPI123Freq_Value,SPI45Freq_Value,SPI6Freq_Value,SWPMI1Freq_Value,SYSCLKFreq_VALUE,SYSCLKSource,Tim1OutputFreq_Value,Tim2OutputFreq_Value,TraceFreq_Value,USART16Freq_Value,USART234578Freq_Value,USBFreq_Value,VCO1OutputFreq_Value,VCO2OutputFreq_Value,VCO3OutputFreq_Value,VCOInput1Freq_Value,VCOInput2Freq_Value,VCOInput3Freq_Value
RCC.LPTIM1Freq_Value=18750000
RCC.LPTIM2Freq_Value=37500000
RCC.LPTIM345Freq_Value=37500000
RCC.LPUART1Freq_Value=37500000
RCC.LTDCFreq_Value=20156250
RCC.MCO1PinFreq_Value=32000000
RCC.MCO2PinFreq_Value=75000000
RCC.PLLFRACN=0
RCC.PLLSourceVirtual=RCC_PLLSOURCE_HSE
RCC.QSPIFreq_Value=75000000
RCC.RNGFreq_Value=48000000
RCC.RTCFreq_Value=32000
RCC.SAI1Freq_Value=50000000
RCC.SAI23Freq_Value=50000000
RCC.SAI4AFreq_Value=50000000
RCC.SAI4BFreq_Value=50000000
RCC.SDMMCFreq_Value=50000000
RCC.SPDIFRXFreq_Value=50000000
RCC.SPI123Freq_Value=50000000
RCC.SPI45Freq_Value=18750000
RCC.SPI6Freq_Value=37500000
RCC.SWPMI1Freq_Value=18750000
RCC.SYSCLKFreq_VALUE=75000000
RCC.SYSCLKSource=RCC_SYSCLKSOURCE_PLLCLK
RCC.Tim1OutputFreq_Value=37500000
RCC.Tim2OutputFreq_Value=37500000
RCC.TraceFreq_Value=75000000
RCC.USART16Freq_Value=18750000
RCC.USART234578Freq_Value=18750000
RCC.USBFreq_Value=50000000
RCC.VCO1OutputFreq_Value=150000000
RCC.VCO2OutputFreq_Value=180000000
RCC.VCO3OutputFreq_Value=40312500
RCC.VCOInput1Freq_Value=2500000
RCC.VCOInput2Freq_Value=10000000
RCC.VCOInput3Freq_Value=312500
SH.S_TIM2_CH1_ETR.0=TIM2_ETR,ClockSourceETR_Mode2
SH.S_TIM2_CH1_ETR.ConfNb=1
SH.S_TIM5_ETR.0=TIM5_ETR,ClockSourceETR_Mode2
SH.S_TIM5_ETR.ConfNb=1
SPI2.BaudRatePrescaler=SPI_BAUDRATEPRESCALER_64
SPI2.CalculateBaudRate=781.25 KBits/s
SPI2.DataSize=SPI_DATASIZE_8BIT
SPI2.Direction=SPI_DIRECTION_2LINES
SPI2.IPParameters=VirtualType,Mode,Direction,CalculateBaudRate,DataSize,BaudRatePrescaler
SPI2.Mode=SPI_MODE_MASTER
SPI2.VirtualType=VM_MASTER
TIM2.ClockFilter=0
TIM2.IPParameters=ClockFilter
TIM6.IPParameters=Prescaler,Period
TIM6.Period=1000
TIM6.Prescaler=75
UART4.BaudRate=115200
UART4.IPParameters=BaudRate,WordLength
UART4.WordLength=WORDLENGTH_8B
USART1.IPParameters=VirtualMode-Asynchronous
USART1.VirtualMode-Asynchronous=VM_ASYNC
USART3.IPParameters=VirtualMode-Asynchronous
USART3.VirtualMode-Asynchronous=VM_ASYNC
USART6.IPParameters=VirtualMode
USART6.VirtualMode=VM_ASYNC
VP_MEMORYMAP_VS_MEMORYMAP.Mode=CurAppReg
VP_MEMORYMAP_VS_MEMORYMAP.Signal=MEMORYMAP_VS_MEMORYMAP
VP_SYS_VS_Systick.Mode=SysTick
VP_SYS_VS_Systick.Signal=SYS_VS_Systick
VP_TIM6_VS_ClockSourceINT.Mode=Enable_Timer
VP_TIM6_VS_ClockSourceINT.Signal=TIM6_VS_ClockSourceINT
board=NUCLEO-H743ZI2
isbadioc=false

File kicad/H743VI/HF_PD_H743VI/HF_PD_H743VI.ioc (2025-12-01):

#MicroXplorer Configuration settings - do not modify
ADC1.Channel-0\#ChannelRegularConversion=ADC_CHANNEL_9
ADC1.IPParameters=Rank-0\#ChannelRegularConversion,master,Channel-0\#ChannelRegularConversion,SamplingTime-0\#ChannelRegularConversion,OffsetNumber-0\#ChannelRegularConversion,OffsetSignedSaturation-0\#ChannelRegularConversion,NbrOfConversionFlag
ADC1.NbrOfConversionFlag=1
ADC1.OffsetNumber-0\#ChannelRegularConversion=ADC_OFFSET_NONE
ADC1.OffsetSignedSaturation-0\#ChannelRegularConversion=DISABLE
ADC1.Rank-0\#ChannelRegularConversion=1
ADC1.SamplingTime-0\#ChannelRegularConversion=ADC_SAMPLETIME_1CYCLE_5
ADC1.master=1
ADC2.Channel-0\#ChannelRegularConversion=ADC_CHANNEL_9
ADC2.IPParameters=Rank-0\#ChannelRegularConversion,Channel-0\#ChannelRegularConversion,SamplingTime-0\#ChannelRegularConversion,OffsetNumber-0\#ChannelRegularConversion,OffsetSignedSaturation-0\#ChannelRegularConversion,NbrOfConversionFlag
ADC2.NbrOfConversionFlag=1
ADC2.OffsetNumber-0\#ChannelRegularConversion=ADC_OFFSET_NONE
ADC2.OffsetSignedSaturation-0\#ChannelRegularConversion=DISABLE
ADC2.Rank-0\#ChannelRegularConversion=1
ADC2.SamplingTime-0\#ChannelRegularConversion=ADC_SAMPLETIME_1CYCLE_5
CAD.formats=
CAD.pinconfig=
CAD.provider=
CORTEX_M7.IPParameters=default_mode_Activation
CORTEX_M7.default_mode_Activation=1
File.Version=6
GPIO.groupedBy=Show All
I2C2.IPParameters=Timing
I2C2.Timing=0x00909FCE
I2C4.IPParameters=Timing
I2C4.Timing=0x109093DC
KeepUserPlacement=false
MMTAppRegionsCount=0
MMTConfigApplied=false
Mcu.CPN=STM32H743VIT6
Mcu.Family=STM32H7
Mcu.IP0=ADC1
Mcu.IP1=ADC2
Mcu.IP10=SPI2
Mcu.IP11=SPI3
Mcu.IP12=SPI4
Mcu.IP13=SYS
Mcu.IP14=TIM2
Mcu.IP15=TIM5
Mcu.IP16=UART4
Mcu.IP17=USART3
Mcu.IP2=CORTEX_M7
Mcu.IP3=DEBUG
Mcu.IP4=I2C2
Mcu.IP5=I2C4
Mcu.IP6=MEMORYMAP
Mcu.IP7=NVIC
Mcu.IP8=RCC
Mcu.IP9=SPI1
Mcu.IPNb=18
Mcu.Name=STM32H743VITx
Mcu.Package=LQFP100
Mcu.Pin0=PE2
Mcu.Pin1=PE3
Mcu.Pin10=PC2_C
Mcu.Pin11=PC3_C
Mcu.Pin12=PA0
Mcu.Pin13=PA1
Mcu.Pin14=PA2
Mcu.Pin15=PA3
Mcu.Pin16=PA4
Mcu.Pin17=PA5
Mcu.Pin18=PA6
Mcu.Pin19=PA7
Mcu.Pin2=PE4
Mcu.Pin20=PB0
Mcu.Pin21=PB2
Mcu.Pin22=PE8
Mcu.Pin23=PE9
Mcu.Pin24=PE10
Mcu.Pin25=PE11
Mcu.Pin26=PE12
Mcu.Pin27=PE13
Mcu.Pin28=PE14
Mcu.Pin29=PE15
Mcu.Pin3=PE5
Mcu.Pin30=PB10
Mcu.Pin31=PB11
Mcu.Pin32=PB12
Mcu.Pin33=PB13
Mcu.Pin34=PB14
Mcu.Pin35=PB15
Mcu.Pin36=PD8
Mcu.Pin37=PD9
Mcu.Pin38=PD10
Mcu.Pin39=PD11
Mcu.Pin4=PE6
Mcu.Pin40=PD12
Mcu.Pin41=PD13
Mcu.Pin42=PD14
Mcu.Pin43=PD15
Mcu.Pin44=PC6
Mcu.Pin45=PC7
Mcu.Pin46=PC8
Mcu.Pin47=PC9
Mcu.Pin48=PA8
Mcu.Pin49=PA9
Mcu.Pin5=PC14-OSC32_IN (OSC32_IN)
Mcu.Pin50=PA10
Mcu.Pin51=PA11
Mcu.Pin52=PA12
Mcu.Pin53=PA13 (JTMS/SWDIO)
Mcu.Pin54=PA14 (JTCK/SWCLK)
Mcu.Pin55=PA15 (JTDI)
Mcu.Pin56=PC10
Mcu.Pin57=PC11
Mcu.Pin58=PD2
Mcu.Pin59=PD3
Mcu.Pin6=PC15-OSC32_OUT (OSC32_OUT)
Mcu.Pin60=PD4
Mcu.Pin61=PD5
Mcu.Pin62=PD6
Mcu.Pin63=PD7
Mcu.Pin64=PB3 (JTDO/TRACESWO)
Mcu.Pin65=PB4 (NJTRST)
Mcu.Pin66=PB5
Mcu.Pin67=PB6
Mcu.Pin68=PB9
Mcu.Pin69=PE0
Mcu.Pin7=PH0-OSC_IN (PH0)
Mcu.Pin70=PE1
Mcu.Pin71=VP_SYS_VS_Systick
Mcu.Pin72=VP_MEMORYMAP_VS_MEMORYMAP
Mcu.Pin8=PC0
Mcu.Pin9=PC1
Mcu.PinsNb=73
Mcu.ThirdPartyNb=0
Mcu.UserConstants=
Mcu.UserName=STM32H743VITx
MxCube.Version=6.12.0
MxDb.Version=DB.6.0.120
NVIC.BusFault_IRQn=true\:0\:0\:false\:false\:true\:false\:false\:false
NVIC.DebugMonitor_IRQn=true\:0\:0\:false\:false\:true\:false\:false\:false
NVIC.ForceEnableDMAVector=true
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

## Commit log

2024-11-03 adding kicad project
    [Input_stage double side.kicad_pcb, Input_stage single side.kicad_pcb, Input_stage-Edge_Cuts.dxf, Input_stage-Edge_Cuts.gm1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]
2024-11-13 try to write read registers, not wirking yet
2025-10-01 some initial commits
    [LF_phase_detector.kicad_pcb]
2025-10-01 new kicad project
    [HF_phase_detector-B_Cu.gbl, HF_phase_detector-B_Fab.gbr, HF_phase_detector-B_Mask.gbs, HF_phase_detector-B_Paste.gbp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]
